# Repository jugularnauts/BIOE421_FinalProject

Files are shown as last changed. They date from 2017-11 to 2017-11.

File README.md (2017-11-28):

## BIOE 421 Final Project: Real-time display tool for venous pulsation data
**A device for real-time visualization and processing of accelerometer and pulse sensor data for Team Jugularnauts, a Rice University senior engineering design team.**

**By Nick Calafat and Angela Zhang
BIOE 421: Microcontroller Applications
Dr. Jordan Miller
Rice University, Fall 2017**

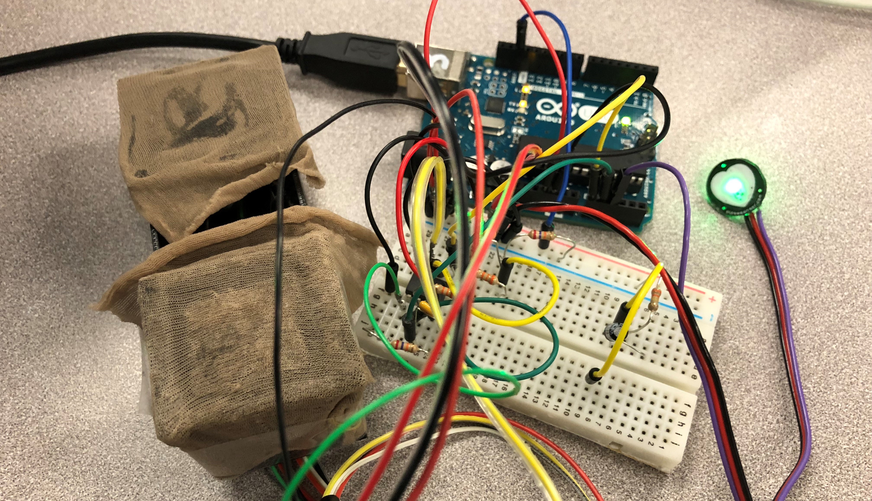
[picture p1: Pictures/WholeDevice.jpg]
photo of whole device


##### Possible features:
- Signal conditioning for improved signal acquisition
- Form factor exploration for reduction of mechanical coupling
- Live display of raw accelerometer data
- Live display of pulse sensor data
- Interactive scaling for graphed data
- ~~Studfinder function for locating strongest pulsation signal~~*
- ~~Signal subtraction of competitor physiological signals (i.e., carotid vs. jugular pulsations)~~*
- ~~Signal processing to isolate jugular vein pulsation~~*

*strikethrough indicates features that were not achieved during the course of this project

### Abstract
This device will serve as a realtime information display for use in developing a device to measure jugular venous pressure, as part of Team Jugularnauts' senior design project. Preliminary prototypes will feature raw data acquisition from a 2x1 accelerometer array and an optical pulse sensor. The accelerometers and pulse sensor will be interfaced with Arduino through analog input pins. Arduino will be used for its precise timing capabilities, which are important for accurate signal subtraction, and will be connected to Raspberry Pi to provide realtime visual display of raw data through a Processing GUI. Future implementations may incorporate other desired features, including signal localization and signal processing. Signal localization may be explored through a “stud finder” mechanism, through which the strength of the signal corresponds to visual feedback on the Processing GUI, allowing the user to place the device correctly over the location of strongest signal (i.e., over the carotid/jugular bundle). Signal processing may be explored for reducing noise and subtracting competing physiologic signals, in order to isolate pulsations of the jugular vein.

### Projected Milestones, Goals, and Due Dates
11/3: Project abstract due
- Publish final abstract to Github
- Prototype Processing GUI visualization using data from single ADXL335 accelerometer

11/9: Initial prototype due
- Prototype visualization with 2x1 accelerometer array
- Implement pulse sensor acquisition and visualization (if parts arrive)
- 3D print casing for device to be used on human neck, rather than affixed to breadboard

11/16: Fit and finish due
- Finalize GUI for visualization of raw signals
- Assemble 3D printed casing and hardware components
- Explore signal localization and subtraction of carotid pulse (heart beat)

11/28: Final code due
- Finalize additional features (signal localization and subtraction)

### Hardware
Our final prototype uses 2 [Adafruit ADXL335 accelerometer](https://www.adafruit.com/product/163) breakout boards, an [Arduino-compatible Pulse Sensor](https://www.adafruit.com/product/1093), and an [Arduino Uno](https://store.arduino.cc/usa/arduino-uno-rev3). We 3D-printed a case to house the accelerometers that also serves to suspend them for free, mechanically isolated movement. This is a critical part of our design since we were trying to measure very small deflections from the jugular vein. The CAD files can be found in the AutoCADFiles folder.

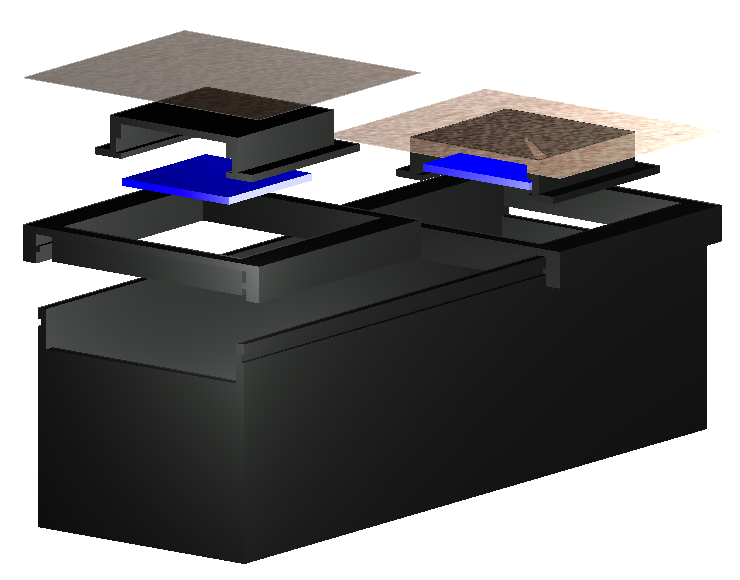
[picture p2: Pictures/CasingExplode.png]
photo of device casing


Applying the device is simple - just hold the casing against the neck so that the accelerometers rest over the jugular vein.

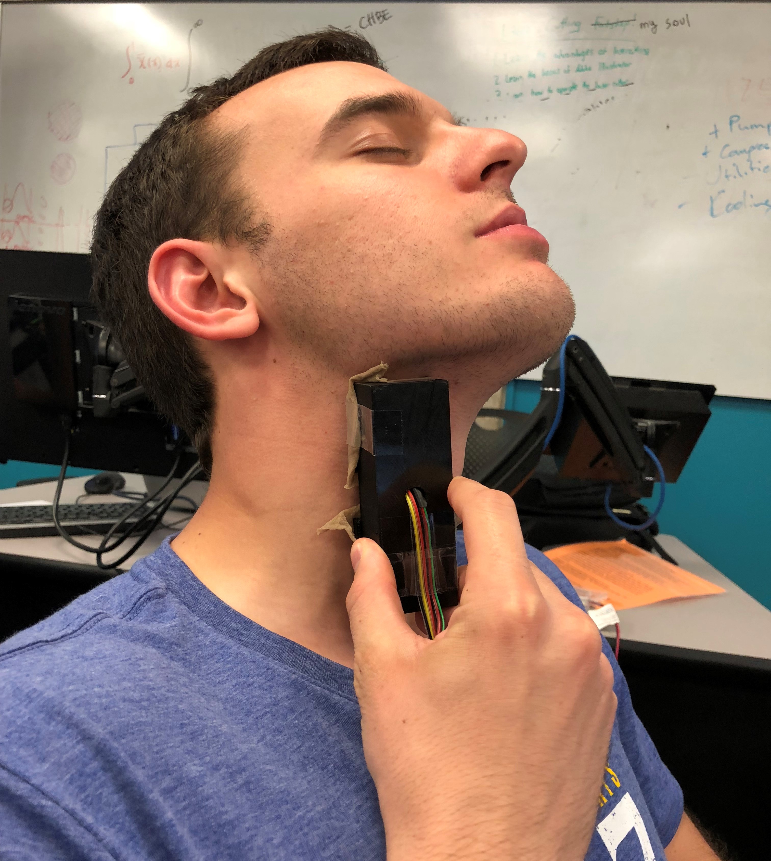
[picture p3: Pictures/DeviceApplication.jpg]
photo of device application


##### Basic Implementation
The ADXL335 breakout boards are designed to receive 5V power, which is regulated onboard to 3.3V. This means that the output signal will be some voltage between 0 and 3.3V. The Pulse Sensor can operate on a 3.3V or 5V supply, giving it a little more flexibility.

However, since the internal voltage reference on Arduino is only 1.1V, the analog reference pin should be used by feeding it a 3.3V supply from one of the ADXL accelerometers. This essentially tells the Arduino's analog to digital converter (ADC) what voltage range to expect from the input signals. Since the Pulse Sensor is referenced to this same voltage, it is essential to power it with 3.3V, even though the accelerometers are powered with 5V. This ensures that all output signals are on the same 0 -- 3.3V range. The wiring diagram for this configuration is presented below.

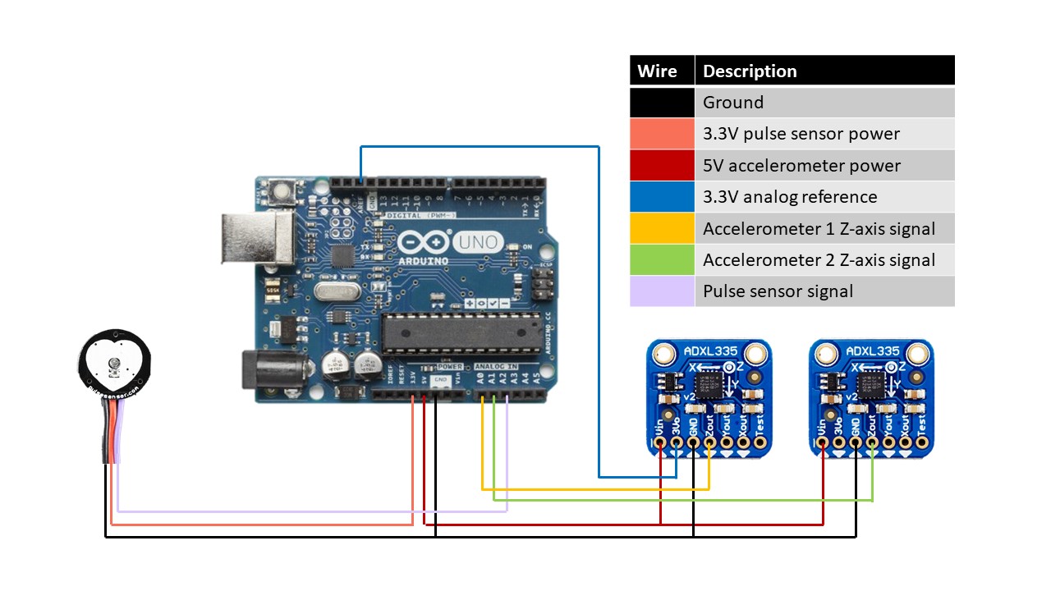
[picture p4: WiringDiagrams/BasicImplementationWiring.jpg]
photo of basic hardware implementation


##### Improving Signal Quality: Filtering and Amplification
One major challenge we faced with this hardware was insufficient resolution. Since the accelerometer breakout boards are fixed at a ±3g acceleration range, the tiny forces produced by the jugular vein yield very small voltage changes from the accelerometers. This, paired with the 10-bit resolution for the Uno's analog input, yields a small signal that approaches the discretization limit of the ADC.

To help solve this problem, we implemented a low-pass filter at 5 Hz to reduce noise and amplified the signal with a gain of 2.2 to bring the signal closer to the 5V maximum range for the ADC.

This also required changes to the previous configuration. Since the new expected voltage range is 5V, the analog reference pin must also be fed 5V. Thus, the Pulse Sensor should also be powered and referenced to 5V. The wiring diagram for this configuration is presented below.

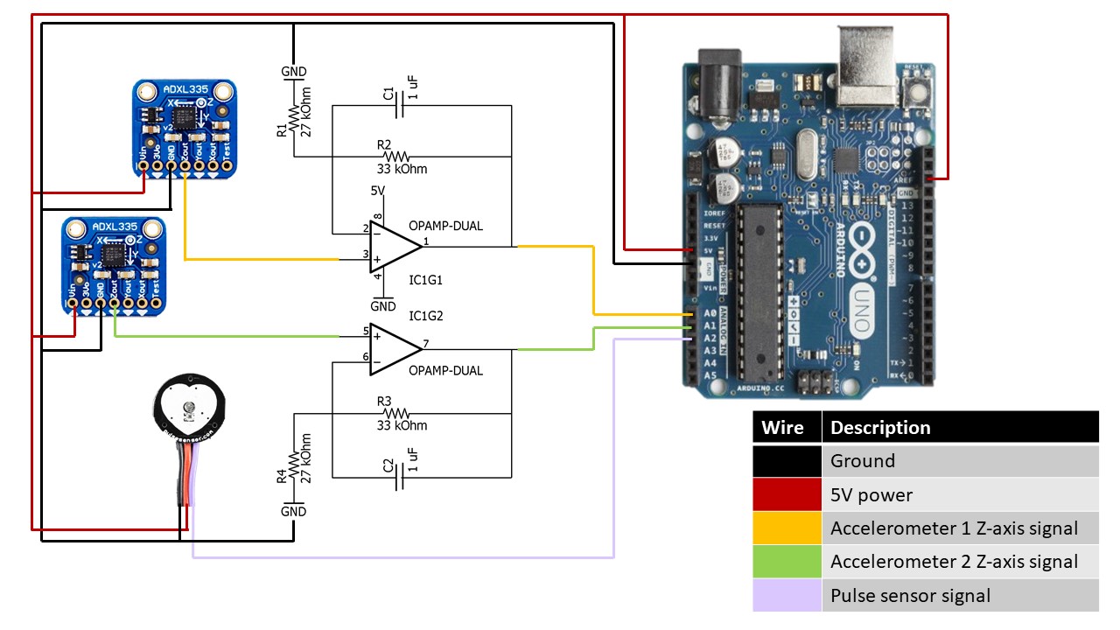
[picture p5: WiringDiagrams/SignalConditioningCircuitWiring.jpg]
photo of conditioning circuit implementation


Notes:
- Gain can be adjusted using G = 1 + R2/R1 for the top circuit or G = 1 + R3/R4 for the bottom circuit
- Cutoff frequency can be adjusted using f = 1/(2 pi R2 C1) for the top circuit, or f = 1/(2pi R3 C2) for the bottom circuit

### Software
We used our Arduino Uno to acquire raw analog signals from the accelerometers and pulse sensor, then sent this data to a Processing interface for real-time visualization of the signals.

##### Arduino
The Arduino sketch reads the raw voltages from each of the 3 sensors and performs sample averaging (n=50) to help smooth the data. Only the z-axis values of the accelerometers were used for ease of prototyping; our initial findings show that this should be sufficient for our purposes. This is what we expected, as the upward pulsation of a vein is primarily in the z-axis of the accelerometer. The sample-averaged data points for each sensor are stored in a string which is sent to Processing via a serial connection.

To change the number of points used in sample averaging, simply change the value of this line in the VenousPulseFirmware.ino sketch:

			// Take multiple samples to reduce noise
			   const int sampleSize = 50;

##### Processing
Processing receives the strings of data from the Arduino Uno and parses them into individual data points. The data for each acceleromter and the pulse sensor are then plotted on a single graph. This graph features a legend with the raw readings from each accelerometer (in mV) and an adjustable y-axis scale. The pulse sensor is plotted in red; accelerometer 1 (yellow wire) in blue; and accelerometer 2 (green wire) in green. The textfields at the top and bottom of the scale allow for user input to adjust the minimum and maximum y values, and thus the range of signal being displayed. These textfields were created with the [ControlP5 library](http://www.sojamo.de/libraries/controlP5/) by Andreas Schlegel. General graphing code was based off of an Arduino example found [here](https://arduining.com/2013/08/05/arduino-and-processing-graph-example/).

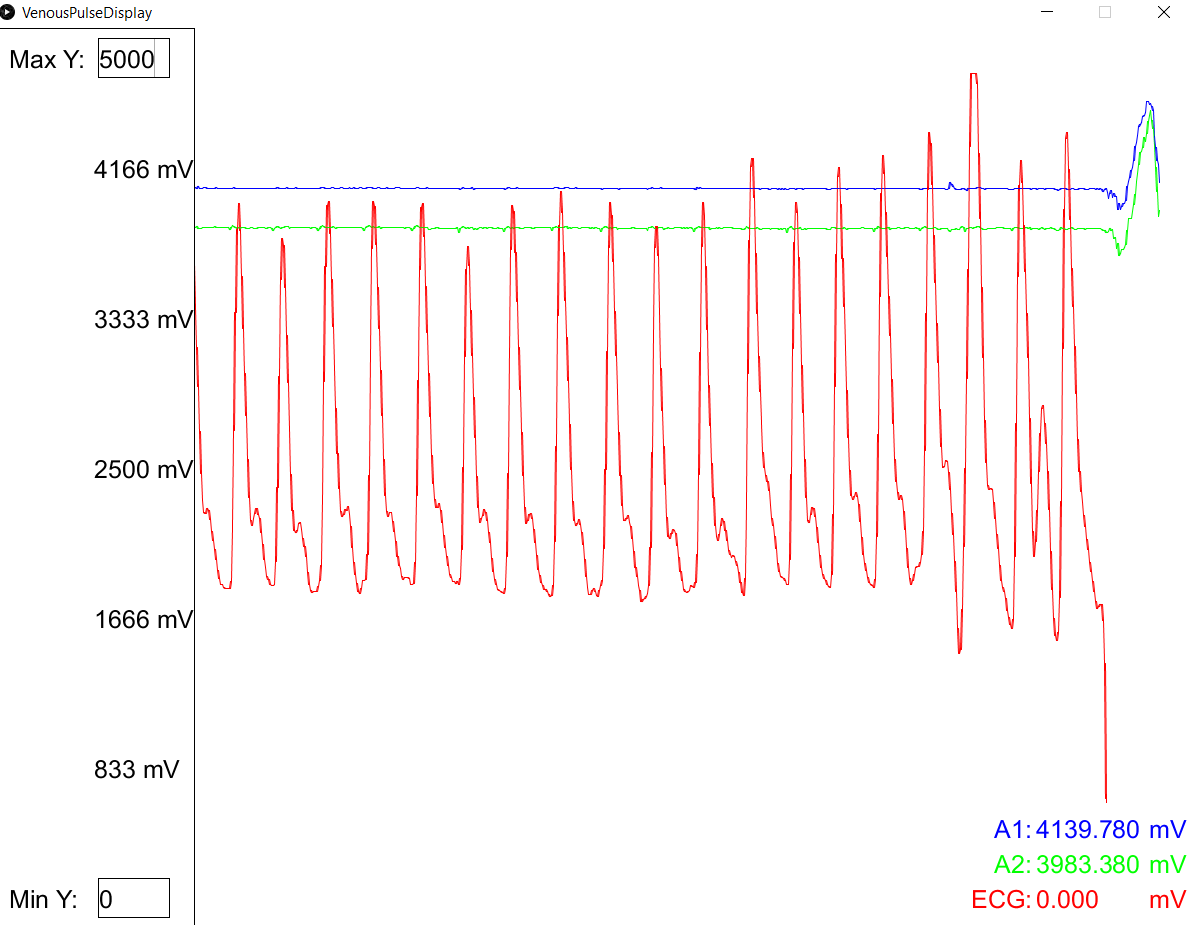
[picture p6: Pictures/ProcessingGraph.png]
screen capture of Processing graph


### Overall Device Function
The flow diagram below illustrates the interactions between hardware and software in this device.
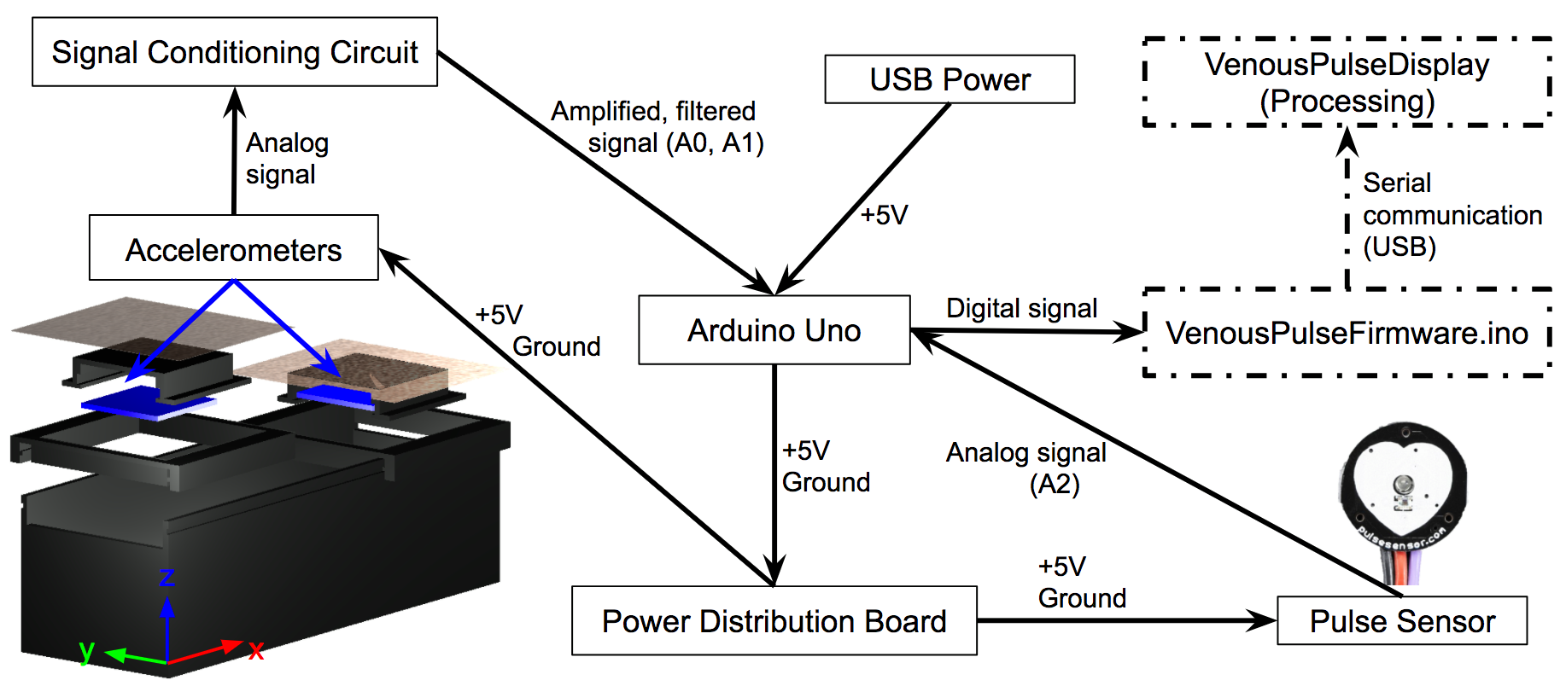
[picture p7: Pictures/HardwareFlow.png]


### Next Steps
- Studfinder function for locating strongest pulsation signal
- Signal subtraction of competitor physiological signals (i.e., carotid vs. jugular pulsations)
- Signal processing to isolate jugular vein pulsation and conversion into pressure measurements
- Explore use of digital accelerometers with higher resolution (>10 bit) and smaller g range (<±3g)
- Explore use of external power supply (>0-5V)

### Acknowledgements
Thanks to Dr. Jordan Miller and Madeleine Gomel for their advice and support throughout this semester.

Thanks to [Arduino](https://www.arduino.cc), [Processing](https://www.processing.org), [Adafruit](https://www.adafruit.com), [World Famous Electronics](https://pulsesensor.com/), and [Andreas Schlegel](http://www.sojamo.de/libraries/controlP5/) for developing the hardware and software we needed to create our device.

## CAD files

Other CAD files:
AutoCADFiles/casing.dwg
AutoCADFiles/casing_explode.dwg

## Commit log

2017-11-02 Adding current Arduino firmware and Processing visualization program
2017-11-14 Updated firmware to acquire from pulse sensor
2017-11-16 Replaced sample averaging with running average to smooth data. Need better SNR to avoid smoothing venous pulsation signal
2017-11-21 Added preamp circuit to hardware, modified firmware and software to acquire and plot voltage rather than acceleration (g)
2017-11-25 Added wiring diagram for basic hardware implementation
2017-11-28 Updated README with final device description, images, flow and wiring diagrams, and CAD files
    [casing.dwg, casing_explode.dwg]
